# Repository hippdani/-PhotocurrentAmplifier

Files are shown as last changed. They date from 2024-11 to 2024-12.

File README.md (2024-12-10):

# Documentation of Photocurrent Sampling Amplifier
## Daniel Hipp, TU Graz 2024
This document contains a detailed description of how to build and use a transimpedance amplifier that is specifically 
tuned to the task of photocurrent sampling (PhotCurrentSampingAmplifier = PCSA). A more concise description containing the minimum information to build and 
operate the device is contained in 
[QuickGuidePCSA_EN.pdf](https://github.com/hippdani/PhotocurrentAmplifier/blob/main/QuickGuidePCSA_EN.pdf).
More information on the design process is available in the bachelor thesis ‘Photocurrent Sampling in free Air’ by 
Daniel Hipp. Files mentioned within the document are available in the repository [PhotocurrentAmplifier](https://github.com/hippdani/PhotocurrentAmplifier).

The intended use of the PCB described in here is to amplify currents produced by a strong laser field that interacts with 
some gas or material. The PCB can be operated in a fine to high vacuum to observe ions of pure gases at low pressures.
The currents are collected at the electrodes A and B and can range from pA to µA according to the amplification gain 
that is chosen. To collect 
these currents, electrodes made out of sheet metal can be soldered onto the gold plated electrodes. To prevent the electrode
elements from acting as antenna, the whole PCB should be placed inside a metal enclosure. A more detailed description of
how to ground the enclosure is contained in chapter 5 of the [documentation](https://github.com/hippdani/PhotocurrentAmplifier/blob/main/PCS_amplifier_docu_EN.pdf)

<p align="center">
  
  <br>
  Fig. 1, Inputs and Outputs on PCB
</p>

The outputs are SMA connectors with a range from +/- 2.5 V, where linearity is guaranteed up to +/- 2 V when connected 
to a load of 1k$\Ohm$ or bigger. 

The PCB displayed above can be populated in several ways to adapt its functionality:
- Electrode A will always be an input, but B can be either:
   - an input @ 0 V bias 
   - an input with a constant bias voltage
   - a bias electrode with fixed voltage 
   - a bias electrode with externally controlled bias voltage
- The transimpedance gain and bandwidth can be set for both channels individually
- A single sided or symmetrical power supply can be used
   - populate PS1 and supply +/- 2.5 V
   - populate PS2 and supply approx. 3.3 V. The negative rail will be created by a charge pump
   
The [documentation](https://github.com/hippdani/PhotocurrentAmplifier/blob/main/PCS_amplifier_docu_EN.pdf) contains detailed information 
on how to choose a configuration and calculate the component values for different gains and bandwidths.

##Low Noise Voltage Supply
To supply a potential free voltage for the PS1 configuration it is advised to either use a battery with a linear 
regulator to maintain 5 V, or a well regulated power supply with little noise. Instructions to build a low noise regulator
suited for both batteries and switch mode power supplies is contained in the folder [LowNoisePSU](https://github.com/hippdani/PhotocurrentAmplifier/tree/main/LowNoisePSU)

##Lock In Amplifier
When used to detect photocurrents generated by a pulsed laser, the signal-to-noise ratio can be vastly improved by 
using a lock in amplifier. This lock in amplifier can be set to the reference frequency of the laser pulses and will
 then reject the noise, that is not pulsed with the reference frequency. Alternatively a Boxcar averager does a similar thing.
If no commercial lock in amplifier or boxcar avergaer is at hand, consider the on described in my other [project](https://github.com/hippdani/lockInAmplifier)
(work in progress)

##Photodiode Amplifier Modification
#TODO
- upload picture / files / BOM
- describe use
- describe the photodiodes

The circuit of the PCSA is also suited to convert the photocurrent of a photodiode with little modifications. 
The modifications are necessary to accomodate the reverse bias voltage that is needed for fast operation of a photodiode.
The high pass filter that blocks out the DC from the bias forms a band pass filter together with the intrinsic low pass 
filter of the transimpedance amplifier.

The high capacity of large are (XUV-) photodiodes limits the achievable bandwidth because stability can not be achieved 
at high frequencies and high gains (Max. gain XX Ohm for Model XY photodiode to achieve 1 MHz -3dB Bandwidth).
Additionally, the large are can act as antenna for stray signals and induce oscillations on its own.
Therefore, proper shielding is required around the photodiode.

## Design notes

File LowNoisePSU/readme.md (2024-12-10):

This folder contains all relevant information to build a small linear regulated and low pass filtered voltage source 
for the photocurrent sampling amplifier. The .zip folder contains everything needed to order the PCB at a manufacturer 
(like JLC PCB, which were successfully used in the past for this design). 

It is intended to connect to a cheap switch 
mode power supply using a barrel jack connector. Such power supplies are readily available but present a lot of 
switching noise on their output. This ciruit is very effective at attenuating the differential mode noise, 
however common mode noise is not addressed.

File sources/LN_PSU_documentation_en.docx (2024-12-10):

# Low Noise Power Supply Documentation

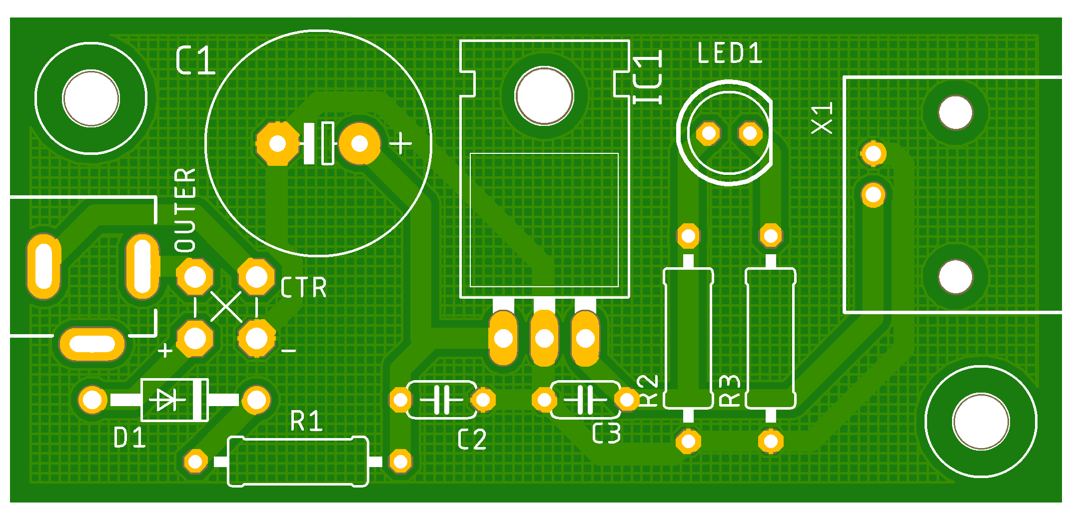
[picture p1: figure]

This PCB contains an RC lowpass filter followed by a linear regulator IC. Its purpose is to generate a stable 5 V from the noisy switch mode power supply input. It is suited to supply 5 V to the photocurrent sampling PCB (Version Jan. 2023 & Dec. 2023) and the XUV photodiode amplifier PCB Version Sep. 2023.

The maximum current that can be supplied by the LM7805 linear regulator is 500 mA. The RC lowpass filter has to be adapted to the actual current consumption of the attached device.

Calculation of R and C depending on the minimal input Voltage U_(in) and the maximum output current I_(out) :

R≤(U_(in) -5.7 V)/(I_(out) ⋅2)

C≥(0.01 s)/R

Recommendation: R=10 Ω, C=1000µF, for U_(in) > 9 V and I_(out) < 100 mA

The circuit is protected against revers polarity by a 1N4007 diode (D1). To match the polarity of the switch mode power supply and the barrel jack input, bridges can be inserted between OUTER and +,- as well as CTR and +,-. The naming OUTER and CTR is not well suited, because not all barrel jacks use the same pinout. It is advised to measure actual the connections.

# Bill of Materials

Part | Name on PCB | Availability at IEP TU Graz
BNC-Jack | X1 | Elektroniker – Lager /
LM7805 | IC1 | Elektroniker – Lager /
Electrolytic Cap. e.g. 1000 µF 25 V | C1 | Elektroniker - Lager /
Ceramic Cap. 100 nF, 50 V | C2, C3
Resistor R1, e.g. 10Ω ¼ W | R1 | Elektroniker - Lager /
Resistor approx. 500Ω ¼ W | R2 | Elektroniker - Lager /
Resistor 1kΩ ¼ W (optional) | R3 | Elektroniker - Lager /
LED 5mm (optional) | LED1 | Elektroniker - Lager /
Diode 1N4004 or 1N4007 | D1 | Elektroniker - Lager /
Barrel Jack | None (Leftmost part) | Bei Platinen / Neuhold
Screw M3x5 up to M3x9 | None | Werkstatt
Screws (2x) M3x15 or M3x20 | None | Werkstatt
3D printed housing | None

# Manufacturing

PCBs can be ordered at JLC PCB for less than 1€ per piece if 10 or more are ordered. (08.2023)
The necessary Eagle / Gerber files are supplied along with this document on Github (https://github.com/hippdani/PhotocurrentAmplifier/LowNoisePSU/LowNoisePSU_2023-09-27.zip)

Add the parts according to the BOM. LED1 and R3 are optional and only necessary if you want a power on indicator.

If less than 100 mA are supplied, bend the legs of IC1 and screw it down when assembling the PCB in the housing. If more than 100 mA are supplied, add heat conducting paste and / or a heatsink.

For mechanical robustness it is advised to glue BNC Jack X1 to the PCB (with CA glue for example). Solder in two bridges according to the polarity of the switch mode power supply used and the specific pinout of the barrel jack. Positive voltage should arrive at the hole marked + and negative at - . Configuration A and B in the following image illustrate the options.

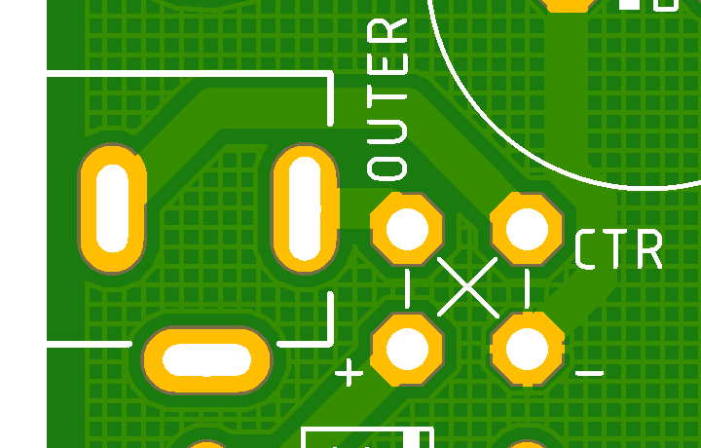
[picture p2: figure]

Print the housing according to the .3mf files (https://github.com/hippdani/PhotocurrentAmplifier/LowNoisePSU/3DPrints)supplied with this document. For better visibility of the power on indicator LED, leave the leads long above the PCB and put a diffuse transparent material onto the hole (e.g. hot glue).

Screw for fastening the PCB and IC1 to the housing: M3x5 up to M3x9

Screws for clamping the two housing halves 2 pcs..: M3x15 or M3x20

It is helpful to mark the finished Device with input voltage and polarity as well as output voltage, current and polarity.

# Electrical Characteristics

- Output voltage: 5 V ±1%, Noise < 600 µVrms typ. If attached to a switch mode PSU, < 300 µVrms typ. If attached to a Battery.
- Minimum input voltage: min. 8 V but more depending on the RC lowpass. Min 9 V if R=10 Ω, C=1000µF, I_(out) < 100 mA
- Maximum input voltage: Max. rating of capacitors or 25 V, whichever is lower.
- Maximum output current: Dictated by lowpass or max. 500 mA dictated by LM7805

# Circuit Diagram

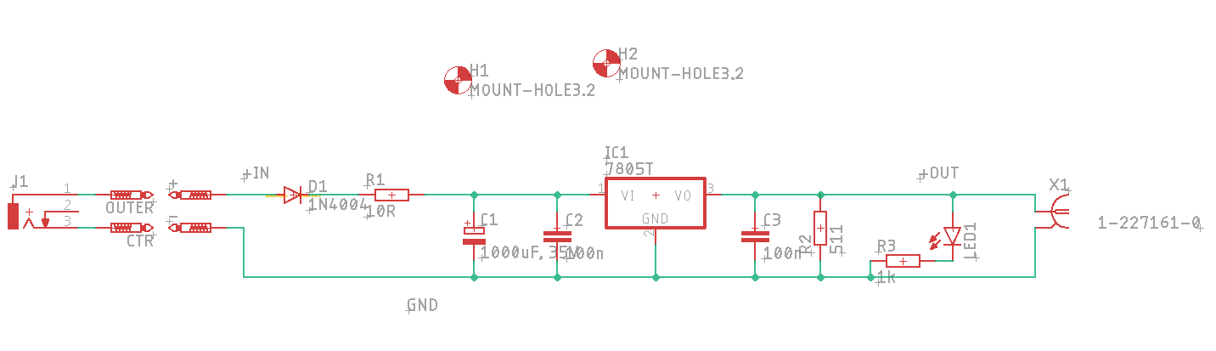
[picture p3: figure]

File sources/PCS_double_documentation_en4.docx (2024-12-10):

# Documentation of Photocurrent Sampling Amplifier

Daniel Hipp, TU Graz 2024

This document contains a detailed description of how to build and use a transimpedance amplifier that is specifically tuned to the task of photocurrent sampling. A more concise description containing the minimum information to build and operate the device is contained in ‘Quick Guide PCS PCB_en.pdf’.
More information on the design process is available in the bachelor thesis ‘Photocurrent Sampling in free Air’. Files mentioned within the document are available in this repository (https://github.com/hippdani/PhotocurrentAmplifier/).

# PCB Layout

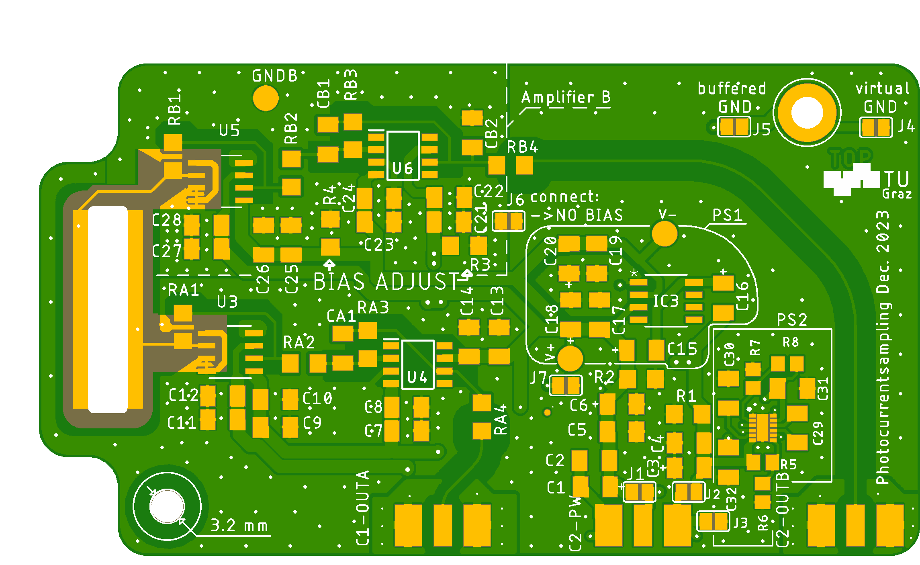
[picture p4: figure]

Electrode A

Electrode B

Output Amplifier A Power Connection Output B or Bias Voltage

The layout and circuit diagram are available as Autodesk Eagle files (PCSoposeLM.brd, PCSoposeLM.sch). In addition, Gerber files are also available in the repository.

# Intended use

The PCB and circuit can be used to amplify currents produced by a strong laser field that interacts with some gas or material (Photo Current Sampling / PCS). The PCB can be operated in a fine to high vacuum to observe ions of pure gases at low pressures.

The currents are collected at the electrodes A and B and can range from pA to µA according to the amplification gain that is chosen. To collect these currents, electrodes made out of sheet metal can be soldered onto the gold-plated electrodes. To prevent the electrode elements from acting as antenna, the whole PCB should be placed inside a metal enclosure.

The outputs are voltages with a range from +/- 2.5 V, provided on the SMA connector that corresponds to the respective amplifier / electrode (A / B). The output voltage is proportional to the input current times the gain that is set by the components. Linearity is guaranteed up to +/- 2 V when connected to a load of 1k$\Ohm$ or bigger.

# Gain Settings

Electrode A and electrode B are each connected to an independent amplification circuit. For both A and B, the same rules apply, therefore the following description uses only the component designations corresponding to A.

The overall gain is the product of the transimpedance of the first stage and the gain of the second stage.

## First Stage

The first stage or input stage consist of a LTC6268-10 in a transimpedance amplifier configuration. The value of the feedback resistor RA1 sets the TIA gain. Bigger RA1 values increase the DC-transimpedance linear, however noise is only increased proportional to √(R_(A1)) . Therefore, SNR (Signal to Noise Ratio) of DC (and slow) signals is improved with increasing RA1. The bandwidth decreases when increasing RA1, however the datasheet of LTC6268-10 is ambiguous about the proportionality:

Equation 1: f_(-3dB) ≈1/(2*π*C_(par) *R_(A1)) (Results some percent better than experiment)

Equation 2: f_(-3dB) ≈√((GBW)/(2*π*C_(par) *R_(A1))) (Results are orders of magnitude away from experiment)

Experiment data is best matched by Equation 1, which is also used for prediction of values. However, the circuit has only been tested up to 10 MHz and effects of GBW are expected to play a significant role at higher frequencies, closer to the GBW.

C_(par) ≈40-60 fF

GBW≈4 GHz (laut LTC6268-10 Datasheet)

SNR of short pulses has to be treated differently than for DC. In photocurrent sampling, packets of charge arrive at the electrodes. This event is typically shorter than what can be resolved by this amplifier and thus produces a smeared-out peak. The integral over one peak created by such an event is proportional to the amount of charge that arrived at the electrode. The signal is therefore typically recorded with a lock-in amplifier or boxcar amplifier. The amplitude of these short pulses is not only governed by the transimpedance, but also depends on the bandwidth of the amplifier, as does the noise. Higher bandwidth leads to shorter and taller peaks and in turn improves SNR.

This effect of increased bandwidth and sharper peaks (according to eq. 1) does almost cancel out the loss of DC gain when reducing RA1. This results in the value of RA1 having little influence on the amplitude of the signal pulses created by short charge packets, as long as the current to the input has a duration << 1/ f_(-3dB) . Smaller values of RA1 still affect DC transimpedance and decrease the visibility of DC input currents as well as increasing the bandwidth.

## Second Stage

Operational amplifier OPA380 in inverting configuration.

The purpose of the second stage is to decouple the sensitive output of the LTC6268-10 from capacitive or ohmic loads presented by the oscilloscope or other instruments attached to the output. At the same time, additional gain and a lowpass filter can be incorporated into the second stage.

Second stage gain: -(R_(A3))/(R_(A2))

Lowpass: f_(-3dB) ≈1/(2*π*R_(A3) *C_(A1))

A sensible approach is to set the corner frequency f_(-3dB) of the lowpass the same as the corner frequency of the first stage. This cuts away only the high frequency noise that does not contain signal. In order to achieve minimal noise while only barely compromising bandwidth, the lowpass corner frequency can be set a little bit below that of the first stage. On the other hand, a reasonable flat transfer curve and low distortion while maintaining good noise figures can be obtained when the lowpass corner frequency is set to about three times that of the first stage. The transfer function can be simulated and optimized using the LT-Spice file ‘2ndStageRCcalculator.asc’.

The values of resistor RA1 and RA2 should be at least 1 kΩ. Much bigger values will introduce additional Johnson-Nyquist noise. CA1 should be a ceramic capacitor with dielectric of type NP0 / C0G.

Overall transimpedance (DC):

Gain=R_(A1) *(R_(A3))/(R_(A2))

Currents flowing into the electrode lead to a positive voltage signal on the output. Note that electrons hitting the electrode cause a technical current flow out of the electrode.

In the following table, suggestions for component values are given. These values can be used as a starting point for experiments. Alternatively, values for various configurations are listed in file ‘Quick Guide PCS PCB_en.pdf’.

Table 1: Suggestions for component values. This will result in approximately 250 kHz bandwidth, DC-transimpedance of 10 MΩ

RA1 | 10MΩ
RA2 | 10kΩ
RA3 | 10kΩ
CA1 | 22pF

# Power Supply Settings

There are three possible ways to supply the circuit with power:

## PS1

PS1 needs a symmetrical voltage supply. The outer conductor of the connector C2-PW carries the negative voltage (-2.5 V) and the inner conductor carries the positive voltage (+2.5 V). A potential free 5V power supply is appropriate for this task, the GND voltage for the circuit is then generated by a TLE2426 rail splitter on the PCB. A well-suited power supply is described in the file ‘LowNoisePSU_doc_en.pdf’XX.

No charge pump (TLE2426) (PS1):

- J1: connect
- J2: connect
- J3: not connect
- J4 = connection of voltage divider GND to housing, OR J5 = buffered GND der of signal output to housing)
- J4 AND J5: connects internal (voltage divider) ground to output ground
- PS2 area (solid line with sharp corners) do not populate.
  - R5-R8 do not populate
  - C29-C32 do not populate
- Input voltage: J2-PW should be connected to 5V low noise voltage source, capable of providing at least 40 mA per populated amplifier (measured: A~33mA, A&B <80mA) The outer conductor of J2-PW (shielding) is at -2,5 V below ground potential, therefore only feedthroughs with floating shield can be used.

Suitable power supply: see LowNoisePSU-DokuXXXXXXX

## PS2

PS2 only requires a positive power supply (approx. 3.3 V) on the inner conductor, the positive and negative voltage of +/- 2.5 V is then generated by an LM27762 charge pump on the circuit board. With this variant, the outer conductor of the power supply has to be grounded.

This version has not been tested in a photo current sampling experiment. It seemingly worked fine in test runs in air with simulated signals. If problems occur, they most likely will stem from the switching frequency of the charge pump. With correct component values and current draw, the switching frequency should be around 2 MHz and should not adversely affect configurations with lower bandwidth.

Charge pump LM27762 (PS2):

- J1: NC
- J2: NC
- J3: connect
- J4: connect
- J5: connect
- J7: connect
- Cxx: Durch Kerko x.xuF ersetzen
- PS1 area (rounded solid line) do not populate
- PS2 area (solid line with sharp corners) populate
- do not populate R1 & R2
- do not populate TLE2624 (=IC3)
- do not populate C15-C20. However, no problem if already populated.
- Input voltage: J2-PW should be connected to a 3-5V voltage source that provides double the current as needed for a PS1 configuration. The outer conductor of J2-PW (shielding) is at ground potential, therefore grounded feedthroughs can be used.

# Bias Settings

No bias = 0 V between both electrodes / both TIA inputs:

In reality there may be a bias voltage corresponding to the difference of the offset voltages of the LTC6268-10. (UOffset << 10mV)

- J6: connect
- R1 & R2 populate both with 1 kΩ
- R3 & R4 (BIAS ADJUST): do not populate OR populate both with 1 kΩ

Fixed Bias:

- J6: NC
- Voltage divider B input bias: + R3—V_B—R4-
- Voltage divider A input bias: + R2—V_B—R1- (A-Bias only possible when using PS1)
- Deviations of the voltage dividers from 1:1 will be visible on the output as a DC component of the signal
- The sum of R of each voltage divider should be around 2 kΩ

U_(Bias_B) =U_(Betrieb) ⋅((R_4)/(R_3 +R_4)-0.5)

B electrode as variable bias:

- do not populate B-amplifier area (dashed line) except for:
- RB1 & RB2 & RB3: 0 Ω Resistor / solder bridge
- RB4 & CB2 form a lowpass to smooth the externally applied voltage. Populate with components of your liking (or choose CB2= 1uF MLCC 16V, RB4 = 10kΩ for a 16 Hz bandwidth)
- External bias can now be applied to J3-OUTB. The maximum voltage is defined by the voltage rating of CB2 but should never exceed 100 V due to sparking tendencies in low pressure atmospheres)

# Grounding

Grounding connection of the enclosure will be established via the gold plated screw hole .

This screw hole can be connected to different potentials via the jumpers J4 and J5.

Without this connection a metallic enclosure will not properly shield the circuit (from experience).

## Without Charge Pump (PS1):

- J4 = rauscharmes Spannungsteiler GND von A Verstärker wenn J6 offen / beiden Verstärkern wenn J6 verbunden ist
- J5 = gebuffertes Ground GND50 (TLE2426 =IC3) das auch an den Ausgängen mit den Shields verbunden ist.

Wenn die Ausgänge mit einem Oszi / Data Logger / etc. verbunden werden, dessen Shield Anschluss geerdet ist, ist das Problem der Masseschleifen zu beachten!

Wenn auch das Platinengehäuße geerdet ist liegt GND50 (Shieldanschluss der Ausgänge) automatisch auf Gehäusepotential. Die Verbindung ist allerdings sehr lang (Platine -> Koax -> Oszi -> Steckdose -> Laborerdung -> Labortisch -> schirmendes Gehäuse) und kann daher Brummen, Rauschen und Schwingen induzieren. Es wird zusätzlich eine kurze Erdungsverbindung z.B. über das Schraubloch und J4 / J5 benötigt. Welche Erdung bessere Ergebnisse erzielt ist noch nicht klar, ausprobieren! Ein Kurzschluss von GND50 und GND (Verbinden von J4 UND J5) ist kein Problem, es kann aber zu zusätzlichem Rauschen und Verzerrungen kommen. Das gilt immer sobald GND mit GND50 verbunden wird, egal ob direkt oder über das Gehäuse und eine Erdschleife die bei den Output Shields endet.

Empfehlung: Isolierte Gehäuse mit GND verbinden (J4 verbinden)

Geerdete Gehäuse mit GND50 verbinden (J5 verbinden) -> Erdschleifen kurz, mit kleiner Fläche und stromlos halten durch optimierte Erdung des Oszis.

## Mit Charge Pump:

Es existiert nur ein GND Potential, dieses kann über J4 und / oder J5 mit dem Gehäuse verbunden werden.

Empfehlung: Gehäuse mit GND50 verbinden (J4 verbinden, J5 verbinden)

Wenn das Gehäuse geerdet ist: Erdschleifen kurz, mit kleiner Fläche und stromlos halten durch optimierte Erdung des Oszis.

# Ein- und Ausgänge: Ratings

### Eingänge / Ausgänge von links nach rechts:

1. Ausgang Verstärker A, Innenleiter Signal, Außenleiter GND50 (Erdung)
2. Stromversorgung, Außenleiter standardmäßig (PS1) -2,5 V, Innenleiter +2,5V Alternativ (PS2): Außenleiter Erdung, Innenleiter 3,3 V
3. Ausgang Verstärker B (Innen / Außen wie A) oder Bias Signal: Außenleiter GND50 (Erdung), Innenleiter Biasspannung

### Ratings:

- Betriebsspannung ohne Charge Pump: min 4 V – max 5,25 V (5V recommended)
- Betriebsspannung mit Charge Pump: min – max V -> V max kann im Vakuum zu thermischer Überlast führen.
- Biasspannung Eingang: wenn anstatt von Verstärker B konfiguriert: Max Rating von CB2 oder max 100V
- Elektroden: Eingangsratings des LTC6268-10 kommen zur Anwendung:
  - „The inputs are protected by two series connected ESD protection

diodes to each power supply. The input current should be limited to less

than 1mA. The input voltage should not exceed 200mV beyond [above or below] the power supply. “

  - “To prevent breakdown of internal devices in the input stage, the two op amp inputs should NOT be separated by more than 2.0V. To help protect the input stage, internal circuitry will engage automatically if the inputs are separated by >2.0V and input currents will begin to flow. In all cases, care should be taken so that these currents remain less than 1mA. Additionally, if only one input is driven, internal circuitry will prevent any breakdown condition under transient conditions. The worst-case differential input voltage usually occurs when the +input is driven and the output is accidentally shorted to ground while in a unity gain configuration.” Die Eingänge können im Fall eines gesättigten Ausganges um mehr als 2 V separiert werden. Die Photoströme sind üblicherweise << 1mA und daher kein Problem, andere Ströme sollten aber unbedingt vermieden werden.
- Stromaufnahme:

Stromanforderungen an den Ausgängen + Ruhestrom:

  - 1 Verstärker, keine Charge Pump: (26 - 35) mA
  - 1 Verstärker, Charge Pump @ 5 V Input:
  - 1 Verstärker, Charge Pump @ 3 V Input:
  - 2 Verstärker, Charge Pump @ 5 V Input:
  - 2 Verstärker, keine Charge Pump: ~64mA ?
- Ausgangscharakteristik:
  - Max. Ausgangsspannung: ±(U_(Betrieb))/2
  - Max. Verzerrungsfreie Ausgangsspannung: ±(U_(Betrieb))/2-0.5 V
  - Max. Ausgangsstrom:
    - 10 mA (Verzerrungsfrei)
    - 50 mA (Reduzierte Verzerrungsfreie Ausgangsspannung)
    - 80 mA(Kurzschluss ohne Charge Pump – ohne Kühlung nur Kurzzeitig erlaubt)
    - 150 mA (Kurzschluss mit Charge Pump – ohne Kühlung nur Kurzzeitig erlaubt)
  - Empfohlener Abschlusswiderstand: >= 1 kΩ
  - Max Kapazität am Ausgang: ~100 pF, abhängig vom Abschlusswiderstand

# Bauteilempfehlungen

Metallfilmwiderstände haben minimales thermisches Rauschen aller erhältlicher SMD-Widerstandsarten. Weil Metallfilmwiderstände jedoch nicht in jeder Größe erhältlich sind, muss man manchmal zu Dünnfilmwiderständen greifen. Diese sind besser als Dickfilmwiderstände. Auf alle 1206 Footprints passen auch 0805 Widerstände. Eine Ausnahme bilden dabei RA1 und RB1, hier muss bei der Montage von 0805 besonders Acht gegeben werden den darunter liegenden Erdungsstreifen nicht zu kontaktieren. 0805 könnte an dieser Position zu erhöhter parasitärer Kapazität und damit kleinerer Bandbreite führen, genau Testergebnisse liegen jedoch nicht vor. Mehr dazu im LTC6268-10 Datasheet und im Demo Manual alias Guideline von LTC.

Alle Kondensatoren im Signalpfad sollten Keramikkondensatoren mit dem Dielektrikum NP0 / C0G sein und ein Spannungsrating >> 10V aufweisen. Kondensatoren auf den Supply Lines sollten möglichst niederohmig sein, dafür sind jeweils Paare aus kleinen Keramikkondensatoren (10 nF, 100 nF) und großen Tantal Elektrolyt Kondensatoren vorgesehen (1 µF, 2.2 µF, 10 µF). Hierbei können alle 2.2 µF Kondensatoren immer auch mit 10 µF bestückt werden.

Die Kondensatoren der Charge Pump (SP2) müssen eigene Kriterien erfüllen
Keramik MLCC X7R mit niedrigem ESR werden im Datenblatt des LM27762 empfohlen.

Der für PS1 benötigte Rail-Splitter IC TLE2426 hat während des Projekts den End-Of-Life Status erreicht und ist nur noch für begrenzte Zeit erhältlich. Ein Vorrat von 10 Stück (Feb. 2024) befindet sich im Büro von Daniel Hipp.

Update Dec. 2024: TLE2426 has status active on Ti product page and is still readily available.

# Jumper Netze

Netznamen: PWR+ …Innenleiter des C2-PWR Eingangs, PWR-….Außenleiter des C“-PWR Eingangs, V+…Positive Spannungsversorgung für Schaltung / ICs, V-…Negative Spannungsversorgung der Schaltung / ICs, GND 50….Außenleiter der Ausgänge(wird bei PS1 von TLE2426 erzeugt), GND Amp.A / Amp. B …. GND um den jeweiligen Verstärker, normalerweise durch Spannungsteiler erzeugt

- J1: verbindet PWR+ mit V+
- J2: verbindet PWR- und V-
- J3: verbindet PWR- und GND Amp. A
- J4: verbindet Schraubloch mit GND von Amp. A (Spannungsteiler-GND)
- J5: verbindet Schraubloch mit GND 50 (von TLE2426 wenn PS1)
- J6: verbindet GND von Amp. A mit GND von Amp. B
- J7: verbindet GND von Amp. A mit GND 50

# Cleaning

Bevor using the PCB in a vacuum environment, cleaning of the flux residues from soldering is necessary to prevent outgassing. Well suited for this task is the PCB cleaner “FLU, FLUXCLENE, FLU400DB” manufactured by Electrolube, which is a solvent spray can with an attached brush to loosen the residue. This rough cleaning should be followed by an ultrasonic cleaning bath in isopropyl alcohol, in order to clean under the chips and other components. After the bath the isopropyl alcohol should be allowed enough time to evaporate bevor putting the PCB in a vacuum. Otherwise boiling of the isopropyl alcohol that may be solved in the polymer casings could cause cracks in the components.

# Version Identification

The PCB discussed in this document is labelled „Photocurrentsampling Dec. 2023“and is displayed in the following figure:

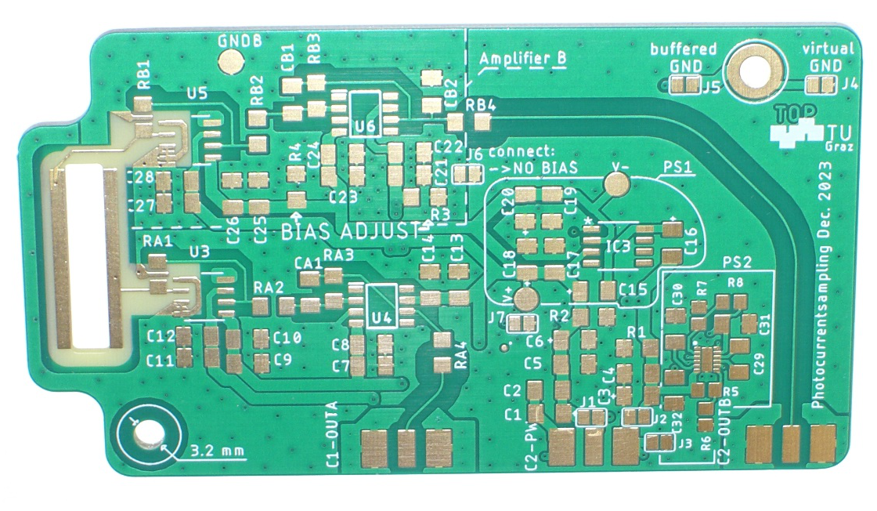
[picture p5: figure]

Die verschiedenen Bestückungsversionen lassen sich anhand der Jumper bzw. der Bestückung unterscheiden. PS1 oder PS2 ist an den entsprechend markierten Bereichen zu erkennen. Ob Amplifier B oder Bias ausgestattet ist, ist im strichlierten Bereich links oben zu erkennen. Wenn nur RB1 – RB4 und CB2 bestückt, dann ist es eine Platine mit externem Bias. Wenn dort auch ICs bestückt sind, ist ein Verstärker B verbaut.

An older version of the PCB, which is functionally identical to a configuration with PS1 and external bias voltage on electrode B is labelled: „V1, Jan. 2023 D. Hipp“. This older version is documented in the bachelor thesis XXXXXXX. The following image shows this version:

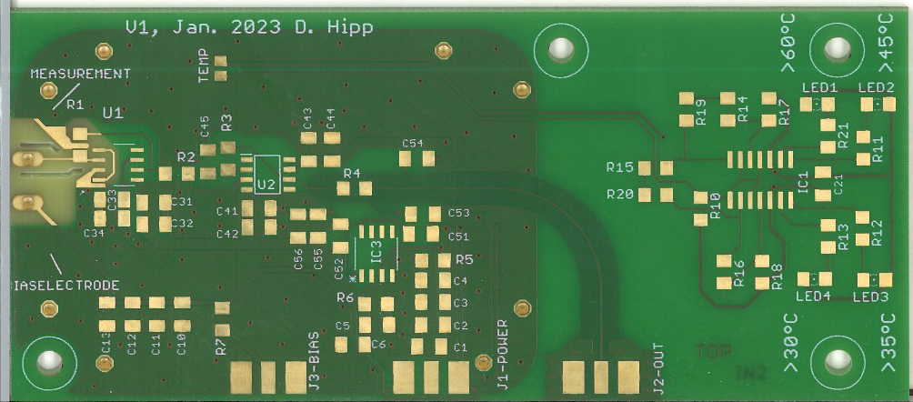
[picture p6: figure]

Both screw holes are on the same positions as in the Version Dec. 2023.

# PCB assembly

Populate the PCB according to the configuration you have chosen. The components are listed in the bill of materials: “BOM_Photocurrentsampling_Double.xlsx”

Sheet metal electrodes can be soldered to the input electrodes. Keep in mind that the material can affect the measurement with its work function and a possibly insulating oxide layer.

Some of the 10 µF capacitors are missing the polarity marking (+) on the PCB silkscreen. The polarity of those is marked in the following picture:

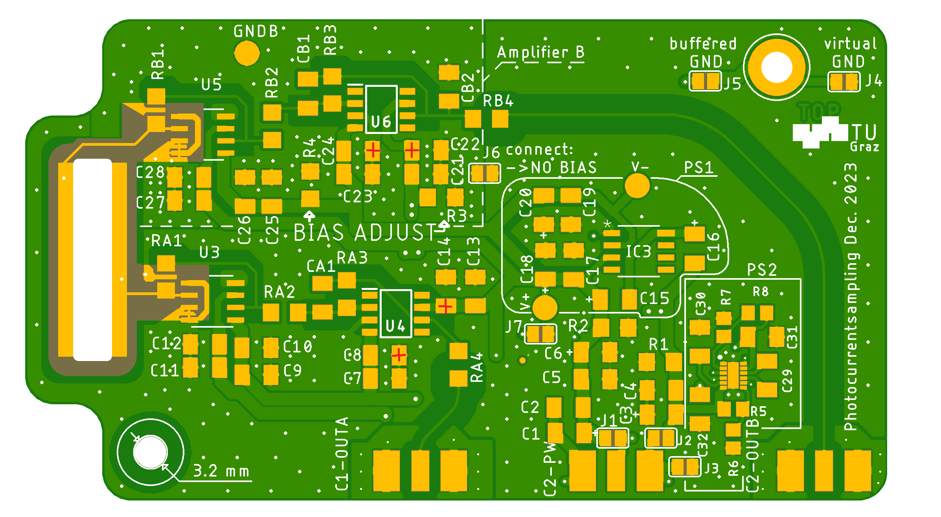
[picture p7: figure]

# ToDo:

- Bilder, bestückt,
- Schaltplan!!!

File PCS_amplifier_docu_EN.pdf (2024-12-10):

# Documentation of Photocurrent Sampling Amplifier

Daniel Hipp, TU Graz 2024

This document contains a detailed description of how to build and use a transimpedance amplifier that is specifically tuned to the task of photocurrent sampling. A more concise description containing the minimum information to build and operate the device is contained in ‘Quick Guide PCS PCB_en.pdf’. More information on the design process is available in the bachelor thesis ‘Photocurrent Sampling in free Air’. Files mentioned within the document are available in this repository. (https://github.com/hippdani/PhotocurrentAmplifier/)

## Content

Reinigung | Fehler! Textmarke nicht definiert.
Versionsidentifikation | Fehler! Textmarke nicht definiert.
Bestückung | Fehler! Textmarke nicht definiert.

## PCB Layout

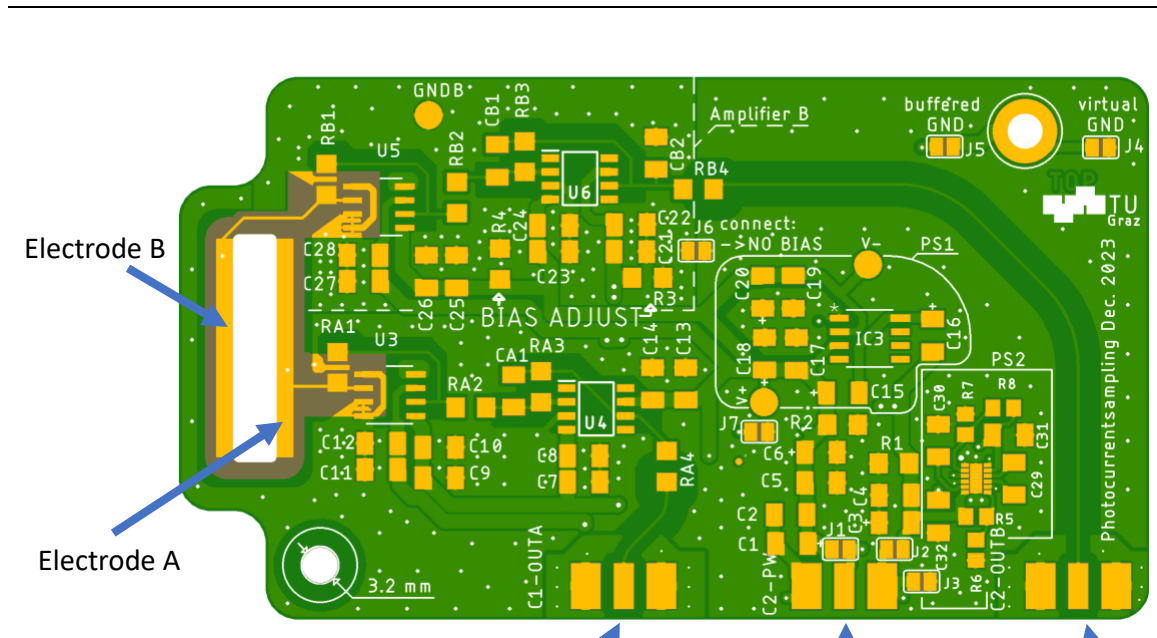
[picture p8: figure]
Electrode A; Electrode B

The layout and circuit diagram are available as Autodesk Eagle files (PCSoposeLM.brd, PCSoposeLM.sch). In addition, Gerber files are also available in the repository.

## Intended use

The PCB and circuit can be used to amplify currents produced by a strong laser field that interacts with some gas or material (Photo Current Sampling / PCS). The PCB can be operated in a fine to high vacuum to observe ions of pure gases at low pressures.

The currents are collected at the electrodes A and B and can range from pA to µA according to the amplification gain that is chosen. To collect these currents, electrodes made out of sheet metal can be soldered onto the gold-plated electrodes. To prevent the electrode elements from acting as antenna, the whole PCB should be placed inside a metal enclosure.

The outputs are voltages with a range from +/- 2.5 V, provided on the SMA connector that corresponds to the respective amplifier / electrode (A / B). The output voltage is proportional to the input current times the gain that is set by the components. Linearity is guaranteed up to +/- 2 V when connected to a load of 1k$\Ohm$ or bigger.

## Gain Settings

Electrode A and electrode B are each connected to an independent amplification circuit. For both A and B, the same rules apply, therefore the following description uses only the component designations corresponding to A.

The overall gain isthe product of the transimpedance of the first stage and the gain of the second stage.

First Stage
The first stage or input stage consist of a LTC6268-10 in a transimpedance amplifier configuration. The value of the feedback resistor RA1 sets the TIA gain. Bigger RA1 values increase the DC-transimpedance linear, however noise is only increased proportional to √RA1. Therefore, SNR (Signal to Noise Ratio) of
Output Amplifier A | Power Connection | Output B or Bias Voltage

DC (and slow) signals is improved with increasing RA1. The bandwidth decreases when increasing RA1, however the datasheet of LTC6268-10 is ambiguous about the proportionality:

Equation 1: f−3dB ≈

1
2∗π∗Cpar∗RA1

(Results some percent better than experiment)

Equation 2: f−3dB ≈ √
GBW
2∗π∗Cpar∗RA1

(Results are orders of magnitude away from experiment)

Experiment data is best matched by Equation 1, which is also used for prediction of values. However, the circuit has only been tested up to 10 MHz and effects of GBW are expected to play a significant role at higher frequencies, closer to the GBW.

Cpar ≈ 40 − 60fF

GBW ≈ 4 GHz (laut LTC6268-10 Datasheet)

SNR of short pulses has to be treated differently than for DC. In photocurrent sampling, packets of charge arrive at the electrodes. This event is typically shorter than what can be resolved by this amplifier and thus produces a smeared-out peak. The integral over one peak created by such an event is proportional to the amount of charge that arrived at the electrode. The signal is therefore typically recorded with a lock-in amplifier or boxcar amplifier. The amplitude of these short pulses is not only governed by the transimpedance, but also depends on the bandwidth of the amplifier, as does the noise. Higher bandwidth leads to shorter and taller peaks and in turn improves SNR.

This effect of increased bandwidth and sharper peaks (according to eq. 1) does almost cancel out the loss of DC gain when reducing RA1. This results in the value of RA1 having little influence on the amplitude of the signal pulses created by short charge packets, as long as the current to the input has a duration << 1/f−3dB. Smaller values of RA1 still affect DC transimpedance and decrease the visibility of DC input currents as well as increasing the bandwidth.

Second Stage
Operational amplifier OPA380 in inverting configuration.

The purpose of the second stage is to decouple the sensitive output of the LTC6268-10 from capacitive or ohmic loads presented by the oscilloscope or other instruments attached to the output. At the same time, additional gain and a lowpass filter can be incorporated into the second stage.

Second stage gain: −

RA3

RA2

Lowpass: f−3dB ≈

1
2∗π∗RA3∗CA1
A sensible approach is to set the corner frequency f−3dB of the lowpass the same as the corner frequency of the first stage. This cuts away only the high frequency noise that does not contain signal. In order to achieve minimal noise while only barely compromising bandwidth, the lowpass corner frequency can be set a little bit below that of the first stage. On the other hand, a reasonable flat transfer curve and low distortion while maintaining good noise figures can be obtained when the lowpass corner frequency is set to about three times that of the first stage. The transfer function can be simulated and optimized using the LT-Spice file ‘2ndStageRCcalculator.asc’.

The values of resistor RA1 and RA2 should be at least 1 kΩ. Much bigger values will introduce additional Johnson-Nyquist noise. CA1 should be a ceramic capacitor with dielectric of type NP0 / C0G.

Overall transimpedance (DC):

Gain = RA1 ∗

RA3

RA2

Currents flowing into the electrode lead to a positive voltage signal on the output. Note that electrons hitting the electrode cause a technical current flow out of the electrode.

In the following table, suggestions for component values are given. These values can be used as a starting point for experiments. Alternatively, values for various configurations are listed in file ‘Quick Guide PCS PCB_en.pdf’.

Table 1: Suggestions for component values. This will result in approximately 250 kHz bandwidth, DC-transimpedance of 10 MΩ

RA1 | 10MΩ
RA2 | 10kΩ
RA3 | 10kΩ
CA1 | 22pF

## Power Supply Settings

There are three possible ways to supply the circuit with power:

PS1
PS1 needs a symmetrical voltage supply. The outer conductor of the connector C2-PW carries the negative voltage (-2.5 V) and the inner conductor carries the positive voltage (+2.5 V). A potential free 5V power supply is appropriate for this task, the GND voltage for the circuit is then generated by a TLE2426 rail splitter on the PCB. A well-suited power supply is described in the file ‘LowNoisePSU_doc_en.pdf’XX.

No charge pump (TLE2426) (PS1):

- J1: connect
- J2: connect
- J3: not connect
- J4 = connection of voltage divider GND to housing, OR J5 = buffered GND der of signal output to housing)
- J4 AND J5: connects internal (voltage divider) ground to output ground
- PS2 area (solid line with sharp corners) do not populate.
- R5-R8 do not populate
- C29-C32 do not populate
- Input voltage: J2-PW should be connected to 5V low noise voltage source, capable of providing at least 40 mA per populated amplifier (measured: A~33mA, A&B <80mA) The outer conductor of J2-PW (shielding) is at -2,5 V below ground potential, therefore only feedthroughs with floating shield can be used.
Suitable power supply: see LowNoisePSU-DokuXXXXXXX

PS2
PS2 only requires a positive power supply (approx. 3.3 V) on the inner conductor, the positive and negative voltage of +/- 2.5 V is then generated by an LM27762 charge pump on the circuit board. With this variant, the outer conductor of the power supply has to be grounded.

This version has not been tested in a photo current sampling experiment. It seemingly worked fine in test runs in air with simulated signals. If problems occur, they most likely will stem from the switching frequency of the charge pump. With correct component values and current draw, the switching frequency should be around 2 MHz and should not adversely affect configurations with lower bandwidth.

Charge pump LM27762 (PS2):

- J1: NC
- J2: NC
- J3: connect
- J4: connect
- J5: connect
- J7: connect
- Cxx: Durch Kerko x.xuF ersetzen
- PS1 area (rounded solid line) do not populate
- PS2 area (solid line with sharp corners) populate
- do not populate R1 & R2
- do not populate TLE2624 (=IC3)
- do not populate C15-C20. However, no problem if already populated.
- Input voltage: J2-PW should be connected to a 3-5V voltage source that provides double the current as needed for a PS1 configuration. The outer conductor of J2-PW (shielding) is at ground potential, therefore grounded feedthroughs can be used.

## Bias Settings

No bias = 0 V between both electrodes / both TIA inputs:

In reality there may be a bias voltage corresponding to the difference of the offset voltages of the LTC6268-10. (UOffset << 10mV)

- J6: connect
- R1 & R2 populate both with 1 kΩ
- R3 & R4 (BIAS ADJUST): do not populate OR populate both with 1 kΩ

Fixed Bias:

- J6: NC
- | Voltage divider B input bias: | + R3—V_B—R4-
- | Voltage divider A input bias: | + R2—V_B—R1- (A-Bias only possible when using PS1)
- Deviations of the voltage dividers from 1:1 will be visible on the output as a DC component of
| the signal
- The sum of R of each voltage divider should be around 2 kΩ

UBiasB = UBetrieb ⋅ (

| | R4
| | R3 + R4 − 0.5)

B electrode as variable bias:

- do not populate B-amplifier area (dashed line) except for:
- RB1 & RB2 & RB3: 0 Ω Resistor / solder bridge
- RB4 & CB2 form a lowpassto smooth the externally applied voltage. Populate with components of your liking (or choose CB2= 1uF MLCC 16V, RB4 = 10kΩ for a 16 Hz bandwidth)
- External bias can now be applied to J3-OUTB. The maximum voltage is defined by the voltage rating of CB2 but should never exceed 100 V due to sparking tendencies in low pressure atmospheres)

## Grounding

Grounding connection of the enclosure will be established via the gold plated screw hole .

This screw hole can be connected to different potentials via the jumpers J4 and J5.

Without this connection a metallic enclosure will not properly shield the circuit (from experience).

Without Charge Pump (PS1):
- J4 = rauscharmes Spannungsteiler GND von A Verstärker wenn J6 offen / beiden Verstärkern wenn J6 verbunden ist
- J5 = gebuffertes Ground GND50 (TLE2426 =IC3) das auch an den Ausgängen mit den Shields verbunden ist.

Wenn die Ausgänge mit einem Oszi / Data Logger / etc. verbunden werden, dessen Shield Anschluss geerdet ist, ist das Problem der Masseschleifen zu beachten!

Wenn auch das Platinengehäuße geerdet ist liegt GND50 (Shieldanschluss der Ausgänge) automatisch auf Gehäusepotential. Die Verbindung ist allerdings sehr lang (Platine -> Koax -> Oszi -> Steckdose -> Laborerdung -> Labortisch -> schirmendes Gehäuse) und kann daher Brummen, Rauschen und Schwingen induzieren. Es wird zusätzlich eine kurze Erdungsverbindung z.B. über das Schraubloch und J4 / J5 benötigt. Welche Erdung bessere Ergebnisse erzielt ist noch nicht klar, ausprobieren! Ein Kurzschluss von GND50 und GND (Verbinden von J4 UND J5) ist kein Problem, es kann aber zu zusätzlichem Rauschen und Verzerrungen kommen. Das gilt immer sobald GND mit GND50 verbunden wird, egal ob direkt oder über das Gehäuse und eine Erdschleife die bei den Output Shields endet.

Empfehlung: Isolierte Gehäuse mit GND verbinden (J4 verbinden)

Geerdete Gehäuse mit GND50 verbinden (J5 verbinden) -> Erdschleifen kurz, mit kleiner Fläche und stromlos halten durch optimierte Erdung des Oszis.

Mit Charge Pump:
Es existiert nur ein GND Potential, dieses kann über J4 und / oder J5 mit dem Gehäuse verbunden werden.

Empfehlung: Gehäuse mit GND50 verbinden (J4 verbinden, J5 verbinden)

Wenn das Gehäuse geerdet ist: Erdschleifen kurz, mit kleiner Fläche und stromlos halten durch optimierte Erdung des Oszis.

## Ein- und Ausgänge: Ratings

Eingänge / Ausgänge von links nach rechts:
1. Ausgang Verstärker A, Innenleiter Signal, Außenleiter GND50 (Erdung)

2. Stromversorgung, | Außenleiter | standardmäßig | (PS1) | -2,5 | V, | Innenleiter | +2,5V
Alternativ (PS2): Außenleiter Erdung, Innenleiter 3,3 V
3. Ausgang Verstärker B (Innen / Außen wie A) oder Bias Signal: Außenleiter GND50 (Erdung), Innenleiter Biasspannung

Ratings:

- Betriebsspannung ohne Charge Pump: min 4 V – max 5,25 V (5V recommended)
- Betriebsspannung mit Charge Pump: min – max V -> V max kann im Vakuum zu thermischer Überlast führen.
- Biasspannung Eingang: wenn anstatt von Verstärker B konfiguriert: Max Rating von CB2 oder max 100V
- Elektroden: Eingangsratings des LTC6268-10 kommen zur Anwendung:
- „The inputs are protected by two series connected ESD protection
diodes to each power supply. The input current should be limited to less
than 1mA. The input voltage should not exceed 200mV beyond [above or below] the power supply. “
- “To prevent breakdown of internal devices in the input stage, the two op amp inputs should NOT be separated by more than 2.0V. To help protect the input stage, internal circuitry will engage automatically if the inputs are separated by >2.0V and input currents will begin to flow. In all cases, care should be taken so that these currents remain less than 1mA. Additionally, if only one input is driven, internal circuitry will prevent any breakdown condition under transient conditions. The worst-case differential input voltage usually occurs when the +input is driven and the output is accidentally shorted to ground while in a unity gain configuration.” Die Eingänge können im Fall eines gesättigten Ausganges um mehr als 2 V separiert werden. Die Photoströme sind üblicherweise << 1mA und daher kein Problem, andere Ströme sollten aber unbedingt vermieden werden.
- Stromaufnahme:
Stromanforderungen an den Ausgängen + Ruhestrom:
- 1 Verstärker, keine Charge Pump: (26 - 35) mA
- 1 Verstärker, Charge Pump @ 5 V Input:
- 1 Verstärker, Charge Pump @ 3 V Input:
- 2 Verstärker, Charge Pump @ 5 V Input:
- 2 Verstärker, keine Charge Pump: ~64mA ?
- Ausgangscharakteristik:
- Max. Ausgangsspannung: ±
| | UBetrieb
| | 2
- Max. Verzerrungsfreie Ausgangsspannung: ±
| | | UBetrieb
| | | 2 | − 0.5 V
- Max. Ausgangsstrom:
- 10 mA (Verzerrungsfrei)
- 50 mA (Reduzierte Verzerrungsfreie Ausgangsspannung)
- 80 mA(Kurzschluss ohne Charge Pump – ohne Kühlung nur Kurzzeitig erlaubt)
- 150 mA (Kurzschluss mit Charge Pump – ohne Kühlung nur Kurzzeitig erlaubt)
- Empfohlener Abschlusswiderstand: >= 1 kΩ
- Max Kapazität am Ausgang: ~100 pF, abhängig vom Abschlusswiderstand

## Bauteilempfehlungen

Metallfilmwiderstände haben minimales thermisches Rauschen aller erhältlicher SMD-Widerstandsarten. Weil Metallfilmwiderstände jedoch nicht in jeder Größe erhältlich sind, muss man manchmal zu Dünnfilmwiderständen greifen. Diese sind besser als Dickfilmwiderstände. Auf alle 1206 Footprints passen auch 0805 Widerstände. Eine Ausnahme bilden dabei RA1 und RB1, hier muss bei der Montage von 0805 besonders Acht gegeben werden den darunter liegenden Erdungsstreifen nicht zu kontaktieren. 0805 könnte an dieser Position zu erhöhter parasitärer Kapazität und damit kleinerer Bandbreite führen, genau Testergebnisse liegen jedoch nicht vor. Mehr dazu im LTC6268-10 Datasheet und im Demo Manual alias Guideline von LTC.

Alle Kondensatoren im Signalpfad sollten Keramikkondensatoren mit dem Dielektrikum NP0 / C0G sein und ein Spannungsrating >> 10V aufweisen. Kondensatoren auf den Supply Lines sollten möglichst niederohmig sein, dafür sind jeweils Paare aus kleinen Keramikkondensatoren (10 nF, 100 nF) und großen Tantal Elektrolyt Kondensatoren vorgesehen (1 µF, 2.2 µF, 10 µF). Hierbei können alle 2.2 µF Kondensatoren immer auch mit 10 µF bestückt werden.

Die | Kondensatoren | der | Charge | Pump | (SP2) | müssen | eigene | Kriterien | erfüllen
Keramik MLCC X7R mit niedrigem ESR werden im Datenblatt des LM27762 empfohlen.

Der für PS1 benötigte Rail-Splitter IC TLE2426 hat während des Projekts den End-Of-Life Status erreicht und ist nur noch für begrenzte Zeit erhältlich. Ein Vorrat von 10 Stück (Feb. 2024) befindet sich im Büro von Daniel Hipp.

Update Dec. 2024: TLE2426 has status active on Ti product page and is still readily available.

## Jumper Netze

Netznamen: PWR+ …Innenleiter des C2-PWR Eingangs, PWR-….Außenleiter des C“-PWR Eingangs, V+…Positive Spannungsversorgung für Schaltung / ICs, V-…Negative Spannungsversorgung der Schaltung / ICs, GND 50….Außenleiter der Ausgänge(wird bei PS1 von TLE2426 erzeugt), GND Amp.A / Amp. B …. GND um den jeweiligen Verstärker, normalerweise durch Spannungsteiler erzeugt

- J1: verbindet PWR+ mit V+
- J2: verbindet PWR- und V-
- J3: verbindet PWR- und GND Amp. A
- J4: verbindet Schraubloch mit GND von Amp. A (Spannungsteiler-GND)
- J5: verbindet Schraubloch mit GND 50 (von TLE2426 wenn PS1)
- J6: verbindet GND von Amp. A mit GND von Amp. B
- J7: verbindet GND von Amp. A mit GND 50

## Cleaning

Bevor using the PCB in a vacuum environment, cleaning of the flux residues from soldering is necessary to prevent outgassing. Well suited for this task is the PCB cleaner “FLU, FLUXCLENE, FLU400DB” manufactured by Electrolube, which is a solvent spray can with an attached brush to loosen the residue. This rough cleaning should be followed by an ultrasonic cleaning bath in isopropyl alcohol, in order to clean under the chips and other components. After the bath the isopropyl alcohol should be allowed enough time to evaporate bevor putting the PCB in a vacuum. Otherwise boiling of the isopropyl alcohol that may be solved in the polymer casings could cause cracks in the components.

## Version Identification

The PCB discussed in this document is labelled „Photocurrentsampling Dec. 2023“and is displayed in the following figure:

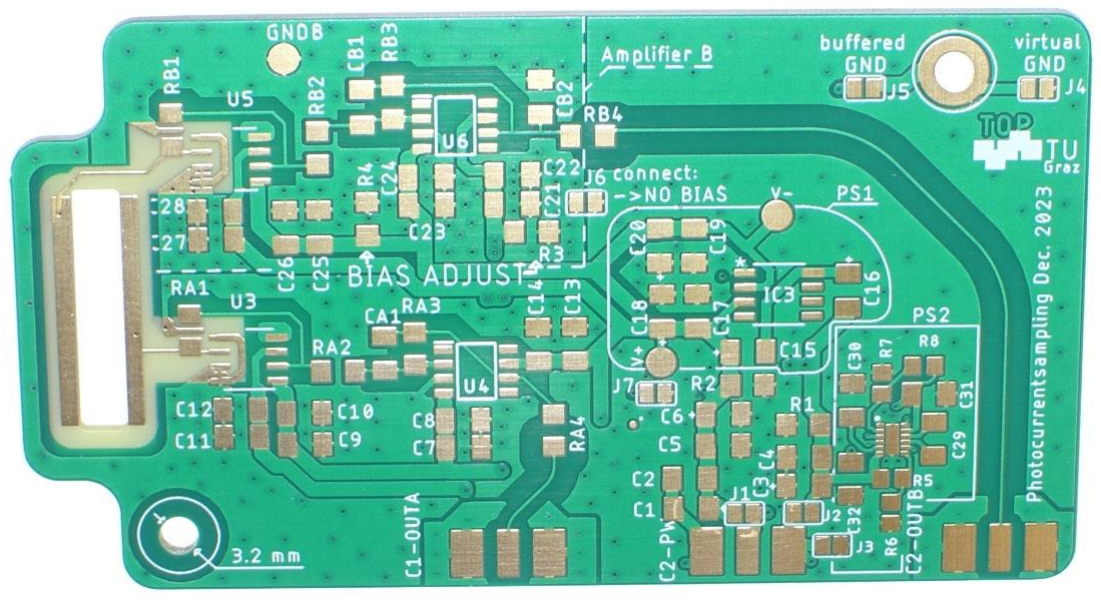
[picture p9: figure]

Die verschiedenen Bestückungsversionen lassen sich anhand der Jumper bzw. der Bestückung unterscheiden. PS1 oder PS2 ist an den entsprechend markierten Bereichen zu erkennen. Ob Amplifier B oder Bias ausgestattet ist, ist im strichlierten Bereich links oben zu erkennen. Wenn nur RB1 – RB4 und CB2 bestückt, dann ist es eine Platine mit externem Bias. Wenn dort auch ICs bestückt sind, ist ein Verstärker B verbaut.

An older version of the PCB, which is functionally identical to a configuration with PS1 and external bias voltage on electrode B is labelled: „V1, Jan. 2023 D. Hipp“. This older version is documented in the bachelor thesis XXXXXXX. The following image shows this version:

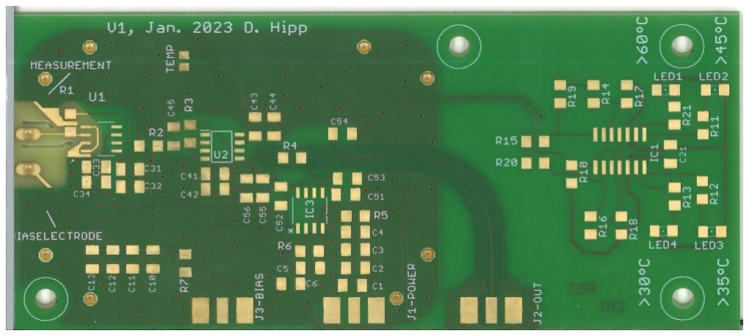
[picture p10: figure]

Both screw holes are on the same positions as in the Version Dec. 2023.

## PCB assembly

Populate the PCB according to the configuration you have chosen. The components are listed in the bill of materials: “BOM_Photocurrentsampling_Double.xlsx”

Sheet metal electrodes can be soldered to the input electrodes. Keep in mind that the material can affect the measurement with its work function and a possibly insulating oxide layer.

Some of the 10 µF capacitors are missing the polarity marking (+) on the PCB silkscreen. The polarity of those is marked in the following picture:

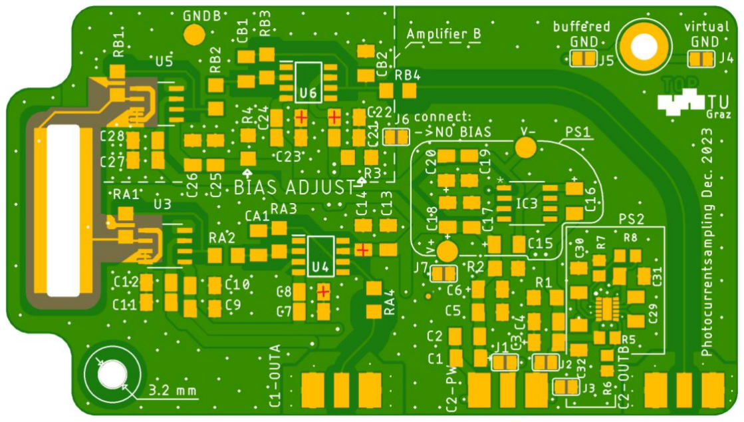
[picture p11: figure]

## ToDo:

- Bilder, bestückt,
- Schaltplan!!!

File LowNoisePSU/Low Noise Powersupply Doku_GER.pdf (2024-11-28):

# Low Noise Power Supply Doku

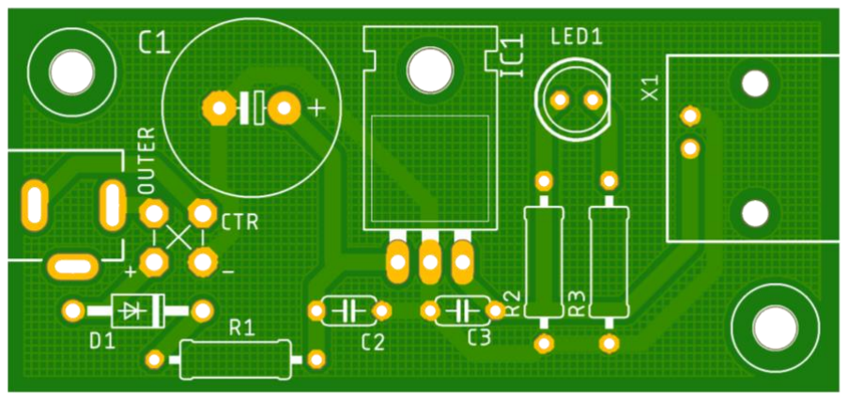
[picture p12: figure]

Es handelt sich hierbei um einen RC-Lowpassfilter mit nachfolgendem Linearregler, um aus der verrauschten Spannung eines Schaltnetzteils glatte 5 V für die Photocurrentsampling Platine oder den XUV Photodioden Verstärker zu erzeugen.

Der RC-Lowpassfilter muss auf den maximal aufkommenden Strom angepasst werden. Der LM7805 Linearregler kann ~500 mA max. liefern.

Berechnung RC in Abhängigkeit von der minimalen Eingangsspannung Uin und des maximalen Ausgangsstromes I_out :

R ≤

Uin − 5.7 V

Iout ⋅ 2

C ≥

0.01 s
R

Empfehlung: R=10 Ω, C=1000µF, für Uin > 9 V und Iout < 100 mA [?-Messung!]

Die Platine wird durch eine 1N4007 Diode vor Verpolung geschützt. Die richtige Polung des Netzteils kann durch einfügen von Brücken bestimmt werden. Dabei die verwendeten Barrel Jack Buchse auszumessen, da der Footprint nicht normiert ist. Die Platinen Beschriftung „OUTER“ und „CTR“ sind daher NICHT GÜLTIG!

## BOM

Bauteil | Bezeichnung | Quelle
BNC-Buchse | X1 | Elektroniker – Lager /
LM7805 | IC1 | Elektroniker – Lager /
Elko 1000 µF XX V | C1 | Elektronik - Lager /
Kerko 100 nF, 50 V | C2, C3
Widerstand R1, z.B. 10Ω ¼ W | R1
Widerstand ca. 500Ω ¼ W | R2
Widerstand 1kΩ ¼ W (optional) | R3
LED 5mm (optional) | LED1
Diode 1N4004 oder 1N4007 | D1
Barrel Jack | Keine | Bei Platinen / Neuhold

## Fertigung

Platinen können bei JLC PCB um <1€ pro Platine bestellt werden, bei Mengen ab ca. 10 Stück. Die nötigen Eagle / Gerber Dateien finden sich im Doku Ordner PCB.

Bestückung laut BOM, LED1 und Vorwiderstand R3 optional. IC1 Pins mit Zange Abwinkeln und bei Montage niederschrauben. Wärmeleitpaste bei I_out > 100 mA empfohlen. BNC-Buchse X1 in Montagelöcher einkleben (z.B. Sekundenkleber, CA). Brücken entsprechend dem verwendeten Netzteil und dem zugehörigen Barrel-Jack so setzen, dass positive Spannung an + liegt und negative am – Anschluss. Konfiguration A und B aus folgendem Bild verdeutlichen die Optionen:

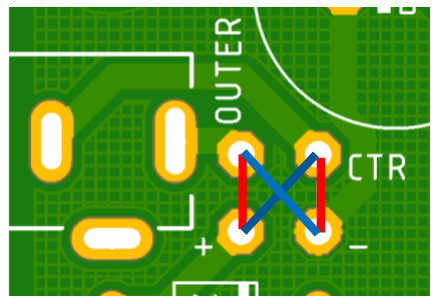
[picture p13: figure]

Gehäuse laut .3mf Files 3D Drucken. Für optimale Sichtbarkeit kann das Loch über der LED mit Heißklebe etc. gefüllt werden, um diffuse Lichtstreuung zu ermöglichen.

Schraube zur Befestigung der Platine im Gehäuse: M3x5 bis M3x9

Gehäuseschrauben 2Stk.: M3x15 oder M3x20

Pickerl mit Eingangsspannung und Ausgangsstrom sowie Steckerpolarität am Gehäuse anbringen.

## Elektrische Charakteristik

- Minimale Eingangsspannung: min. 8 V oder was durch den Lowpass und den Stromverbrauch vorgegeben wird.
- Maximale Eingangsspannung: Max Rating der Kondensatoren oder 25 V (maximum des LM7805)
- Ausgangsspannung: 5 V ± XX%, Rauschen < 600 µVrms typ. (Eine geregelte Batteriespannung hat nocheinmal ca. 50% weniger Rauschen!)
- Maximaler Ausgangsstrom: Durch Lowpass vorgegeben oder max. 500mA des LM7805.

## Schaltplan

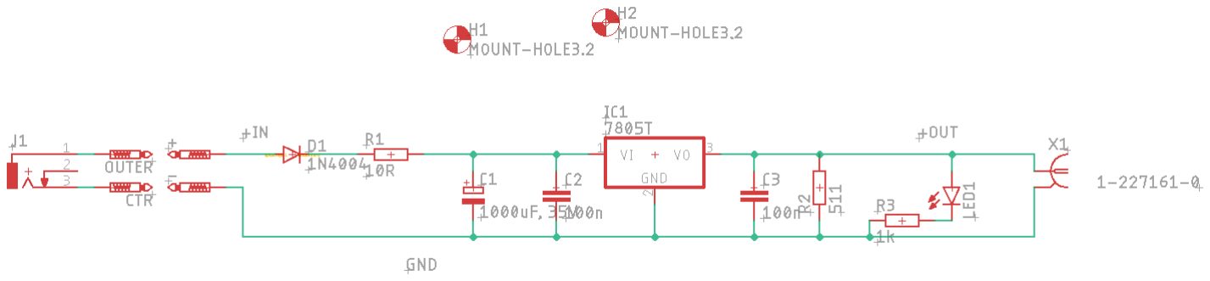
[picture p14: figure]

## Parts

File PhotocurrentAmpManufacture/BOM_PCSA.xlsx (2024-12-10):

() = variable |  | [] = optional / alternative |  | Powersupply options PS1 / PS2 | Jumper open = n, Jumper connected = y
Qty | Value | Device | Package | Parts | Description | Hersteller Nr.
2 | (10M) (100k - 100M) | R-EU_R1206 | R1206 | RA1, RB1 | Precision, thinfilm or metalfilm | ERA8AEB105V / MCA1206MD1005BP100
2 | (10k) (1k-100k) | R-EU_R1206 | R1206 | RA2, RB2 | 2nd Stage amplification feedback resistor
2 | (10k) (1k-100k) | R-EU_R1206 | R1206 | RA3, RB3 | 2nd Stage amplification feedback resistor
1 | [0-100nF] | C-EUC1206K | C1206K | CB2 | Bias Low Pass filter if no Amp2 installed
2 | (22pF) | C-EUC1206K | C1206K | CA1, CB1 | NP0 feedback kerko
2 | 50R | R-EU_R1206 | R1206 | RA4, RB4 | 47R-53R impedance matching resistor
13 | 100n | C-EUC1206K | C1206K | C2, C4, C5, C7, C9, C11, C13, C17, C19, C21, C23, C25, C27 | 10% 50V X7R | C1206C104K5RACAUTO
4 | 10n | C-EUC1206K | C1206K | C10, C12, C26, C28 | 10% 50V X7R | C1206C103K5RACTU
9 | 10uF | C-EU_POL / C-EUC1206K | C1206K | C8, C14, C22, C24, C1, C3, C6, C18, C20 | Tantal elko 1206 | TPSA106K010R0900
4 | 1k | R-EU_R1206 | R1206 | R1, R2, R3, R4 | Precision 1k 0.1% (Metalfilm, Thinfilm) | ERA8AEB102V
2 | LTC6268HS8-10PBFSO-8_S-L | LTC6268HS8-10PBFSO-8_S-L | SO-8_S-L | U3, U5
2 | OPA380AID | OPA380AID | SOIC127P600X175-8N | U4, U6 | Texas Instruments OPA380AI | OPA380AID
3 | SMA Jack | 73251-2123 | 73251-2123 | C1-OUTA, C2-OUTB, C2-PW | SMA Jack PCB Edge Mount 50 | 526-5785
4 | [100k @ PS2] | R-EU_R0805 | R0805 | R5, R6, R7, R8
3 | [1u @ PS2] | C-EUC1206K | C1206K | C29, C31, C32 | kerko switching
1 | [4.7u @ PS2] | C-EUC1206K | C1206K | C30
1 | [LM27762DSSR @ PS2] | LM27762DSSR | SON50P200X300X80-13N | PS2 | LDO Voltage Regulators and neg. switching | LM27762DSSR
2 | [1u @ PS1] | C-EU_POL | C1206K | C15, C16 | Tantal elko 1206 | TPSA105K035R3000
1 | [TLE2426 @ PS1] | TLE2426CDD8-M | D8-M | IC3
7 | () | Jumper |  | J1, J2, J3, J4, J5, J6, J7 | Select appropriate Jumpers
6 | () | Jumper PS1 |  | J1=y, J2=y, J3=n, J4 OR J5, J7=IF J4 AND J5 | Select appropriate Jumpers
6 | () | Jumper PS2 |  | J1=n, J2=n, J3=y, J4=y, J5=y, J7=y | Select appropriate Jumpers
1 | () | Jumper Amp A & B |  | J6=y | Select appropriate Jumpers
1 | () | Jumper Amp A & ext. Bias |  | J6=y | Select appropriate Jumpers
1 | () | Jumper Amp A & int. Bias |  | J6=n | Select appropriate Jumpers

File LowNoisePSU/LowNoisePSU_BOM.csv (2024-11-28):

Part | Value | Device | Package | Description
+ | PTR1PAD1-13 | PTR1PAD1-13 | P1-13 | TEST PIN
- | PTR1PAD1-13 | PTR1PAD1-13 | P1-13 | TEST PIN
C1 | 1000uF, 35V | CPOL-EUE5-13 | E5-13 | POLARIZED CAPACITOR, European symbol
C2 | 100n | C-EU050-024X044 | C050-024X044 | CAPACITOR, European symbol
C3 | 100n | C-EU050-024X044 | C050-024X044 | CAPACITOR, European symbol
CTR | PTR1PAD1-13 | PTR1PAD1-13 | P1-13 | TEST PIN
D1 | 1N4004 | 1N4004 | DO41-10 | DIODE
H1 | MOUNT-HOLE3.2 | MOUNT-HOLE3.2 | 3,2 | MOUNTING HOLE with drill center marker
H2 | MOUNT-HOLE3.2 | MOUNT-HOLE3.2 | 3,2 | MOUNTING HOLE with drill center marker
IC1 | 7805T | 7805T | TO220H | Positive VOLTAGE REGULATOR
J1 |  | DCJ0303 | DCJ0303 | DC POWER JACK
LED1 |  | LED5MM | LED5MM | LED
OUTER | PTR1PAD1-13 | PTR1PAD1-13 | P1-13 | TEST PIN
R1 | 10R | R-EU_0309/12 | 0309/12 | RESISTOR, European symbol
R2 | 511 | R-EU_0309/12 | 0309/12 | RESISTOR, European symbol
R3 | 1k | R-EU_0309/12 | 0309/12 | RESISTOR, European symbol
X1 | 1-227161-0 | 1-227161-0 | AMP_227161 | JACK, RIGHT ANGLE, 50 OHM, PCB, BNC

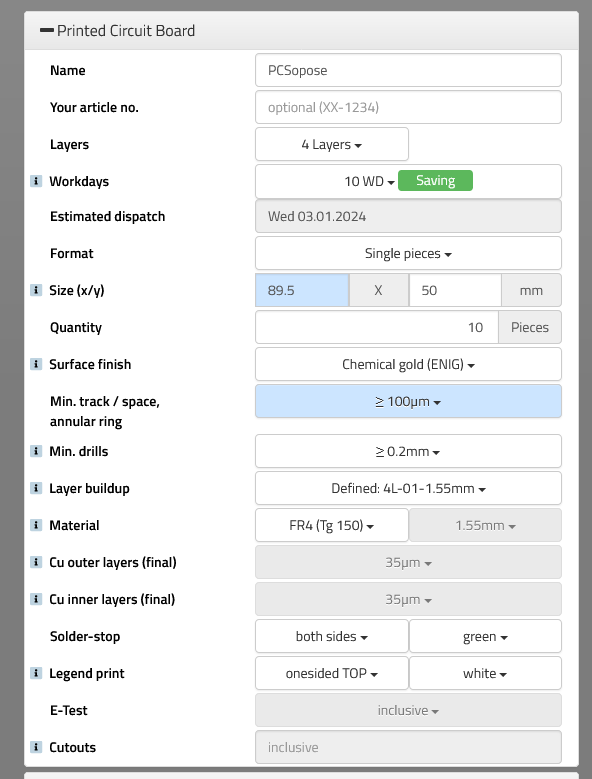
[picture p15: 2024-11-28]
PhotocurrentAmpManufacture/multicbOrderSettings.png

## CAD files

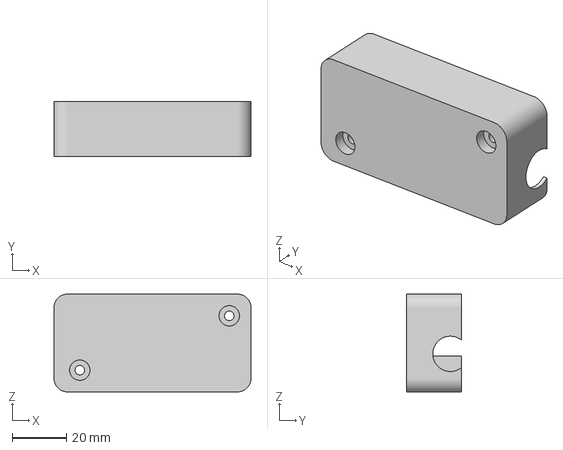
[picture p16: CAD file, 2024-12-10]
LowNoisePSU/3Dprints/BottomClampshellV2.3mf
72.5 x 20.1 x 36.0 mm

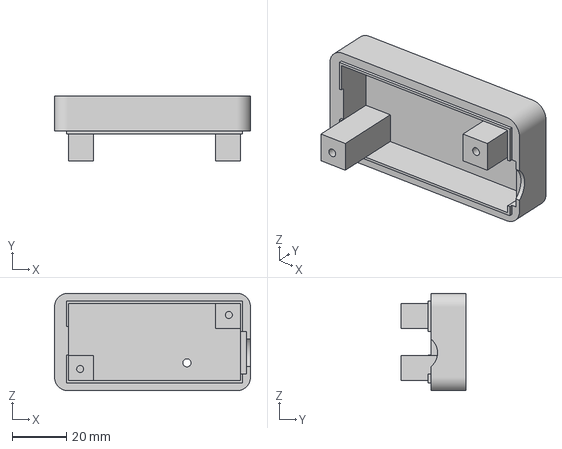
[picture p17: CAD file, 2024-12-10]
LowNoisePSU/3Dprints/TopClampshellV2.3mf
72.5 x 24.0 x 36.0 mm

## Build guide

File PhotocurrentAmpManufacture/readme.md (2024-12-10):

This folder contains all the necessary information to order the photocurrent amplifier PCB from a PCB manufacturer. 
The eagle files were used successfully to order the PCB at [multi-cb](https://www.multi-circuit-boards.eu/index.html), 
using the order details shown in this [Screenshot](https://github.com/hippdani/PhotocurrentAmplifier/multicbOrderSettings). 

The gerber files should be universally accepted by any PCB manufacturer.

The BOM contains parts for different configurations of the circuit, which ones are necessary for your build can be 
determined according to the information in [PCS_Doku](https://github.com/hippdani/PhotocurrentAmplifier/PCS_Docu.pdf). Alternatively, one of the precalculated configurations from 
the [QuickGuide](https://github.com/hippdani/PhotocurrentAmplifier/QuickGuide.pdf) can be used

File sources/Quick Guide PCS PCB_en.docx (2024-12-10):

# Quick Guide Photocurrentsampling PCB

PCB Version Dec. 2023

PCB Layout


Electrode A

Electrode B

Output Amplifier A Power Connection Output B or Bias Voltage

Each chapter of this quick guide contains all the information necessary to build and operate the circuit with the specific setting.

# Standard setting with 2 amplifiers:

~250 kHz bandwidth, DC-transimpedance of 10 MΩ, no bias between electrodes, currents of both A & B electrodes are measured.

Connect Power to the central SMA Jack. +2.5. V on the inner connector, -2.5 V on the outer side (shield). This is the same as 5V supply with positive center that is potential free, e.g. a battery or the low noise power supply described in ‘LN_PSU_documentation_en’.

The Signals are distortion free between +/- 2V but can reach up and down to the supply voltages. Terminate only with >= 1 kΩ. 1MΩ Inputs are fine without termination if the cables used are not too long.

The jumpers J4, J5 and J7 allow different grounding configurations, e.g. separating the input stage ground plane from the housing and SMA shield ground. More information on this is available in the full documentation ‘PCS_double_documentation_en’. A configuration that always works, but may be not the best solution in terms of noise is closing (connecting) jumper J4, J5 and J7.

Table 1: Bill of materials for measurement on both electrodes, ~250 kHz bandwidth, DC-transimpedance of 10 MΩ, no bias between electrodes

Qty | Value | Device | Package | Parts | Description | Hersteller Nr.
2 | 10M | R-EU_R1206 | R1206 | RA1, RB1 | Precision, thinfilm or metalfilm | ERA8AEB105V / MCA1206MD1005BP100
2 | 10k | R-EU_R1206 | R1206 | RA2, RB2 | 2nd Stage amplification feedback resistor
2 | 10k | R-EU_R1206 | R1206 | RA3, RB3 | 2nd Stage amplification feedback resistor
2 | 22pF | C-EUC1206K | C1206K | CA1, CB1 | NP0 feedback ceramic cap.
2 | 50R | R-EU_R1206 | R1206 | RA4, RB4 | 47R-53R impedance matching resistor
13 | 100n | C-EUC1206K | C1206K | C2, C4, C5, C7, C9, C11, C13, C17, C19, C21, C23, C25, C27 | 10% 50V X7R | C1206C104K5RACAUTO
4 | 10n | C-EUC1206K | C1206K | C10, C12, C26, C28 | 10% 50V X7R | C1206C103K5RACTU
9 | 10uF | C-EU_POL / C-EUC1206K | C1206K | C8, C14, C22, C24, C1, C3, C6, C18, C20 | Tantal electrolytic capacitor 1206 | TPSA106K010R0900
4 | 1k | R-EU_R1206 | R1206 | R1, R2, R3, R4 | Precision 1k 0.1% (metalfilm, thinfilm) | ERA8AEB102V
2 | LTC6268HS8-10 | LTC6268HS8-10 | SO-8_S-L | U3, U5
2 | OPA380AID | OPA380AID | SOIC | U4, U6 | Texas Instruments OPA380AI | OPA380AID
3 | SMA Jack | 73251-2123 | | C1-OUTA, C2-OUTB, C2-PW | SMA Jack PCB Edge Mount 50 | 526-5785
2 | 1u | C-EU_POL | C1206K | C15, C16 | Tantal electrolytic capacitor 1206 | TPSA105K035R3000
1 | TLE2426 | TLE2426CDD8-M | D8-M | IC3
6 | () | Jumper PS1 | | J1=y, J2=y, J3=n, J4 OR J5, J7=IF J4 AND J5 | Select appropriate Jumpers
1 | () | Jumper Amp A & B | | J6=y | Select appropriate Jumpers

# Standard setting with 1 Amplifiers + external bias:

~250 kHz bandwidth, DC-transimpedance of 10 MΩ, current of A electrode is measured, connector B is bias input.

Connect Power to the central SMA Jack. +2.5 V on the inner connector, -2.5 V on the outer side (shield). This is the same as 5V supply with positive center that is potential free, e.g. a battery or the low noise power supply described in LN_PSU_documentation_en.

The Signal is on the Left connector (A). It is distortion free between +/- 2V but can reach up and down to the supply voltages. Terminate only with >= 1 kΩ. 1MΩ Inputs are fine without termination if the cables used are not too long.

The jumpers J4, J5 and J7 allow different grounding configurations, e.g. separating the input stage ground plane from the housing and SMA shield ground. More information on this is available in the full documentation ‘PCS_double_documentation_en’. A configuration that always works, but may be not the best solution in terms of noise is closing (connecting) jumper J4, J5 and J7.

Bias can be applied to the rightmost connector (B). The shield of the connector is grounded, the inner contact carries the bias voltage. It should stay within 100V and within the voltage rating of CB2. The bias signal is lowpass-filtered by CB2 and RB4 if RB4 is not 0R.

The corner frequency of this RC lowpass is calculated by following formula:

f_(-3db) =1/(2π R_(B4) C_(B2))

The reason for the lowpass filter is to reduce high frequency noise that would create a current between the electrodes, because they form a plate capacitor. If the bias voltage will be modulated, it is important to choose a corner frequency that is much higher than the modulation frequency.

Table 2: Bill of materials for measurement on one electrode and external bias, ~250 kHz bandwidth, DC-transimpedance of 10 MΩ, bias supplied on connector B

Qty | Value | Device | Package | Parts | Description | Hersteller Nr.
2 | 10M | R-EU_R1206 | R1206 | RA1 | Precision, thinfilm or metalfilm | ERA8AEB105V / MCA1206MD1005BP100
2 | 10k | R-EU_R1206 | R1206 | RA2 | 2nd Stage amplification feedback resistor
2 | 10k | R-EU_R1206 | R1206 | RA3 | 2nd Stage amplification feedback resistor
1 | 100nF C0G | C-EUC1206K | C1206K | CB2 | Bias Low Pass filter if no Amp2 installed
2 | 22pF | C-EUC1206K | C1206K | CA1 | NP0 feedback ceramic cap.
4 | 0R | | 1206 | RB1, RB2, RB3 | 0R Jumpers or solder bridges
| 0R – 10k | | 1206 | RB4 | Bias lowpass together with CB2 or just 0R when no Lowpass is needed
2 | 50R | R-EU_R1206 | R1206 | RA4 | 47R-53R impedance matching resistor
13 | 100n | C-EUC1206K | C1206K | C2, C4, C5, C7, C9, C11, C13, C17, C19, C21, C23, C25, C27 | 10% 50V X7R | C1206C104K5RACAUTO
4 | 10n | C-EUC1206K | C1206K | C10, C12, C26, C28 | 10% 50V X7R | C1206C103K5RACTU
9 | 10uF | C-EU_POL / C-EUC1206K | C1206K | C8, C14, C22, C24, C1, C3, C6, C18, C20 | Tantal electrolytic capacitor 1206 | TPSA106K010R0900
4 | 1k | R-EU_R1206 | R1206 | R1, R2, R3, R4 | Precision 1k 0.1% (Metalfilm, Thinfilm) | ERA8AEB102V
2 | LTC6268HS8-10 | LTC6268HS8-10 | SO-8_S-L | U3, U5 | | LTC6268HS8-10
2 | OPA380AID | OPA380AID | SOIC | U4, U6 | Texas Instruments OPA380AI | OPA380AID
3 | SMA Jack | 73251-2123 | 73251-2123 | C1-OUTA, C2-OUTB, C2-PW | SMA Jack PCB Edge Mount 50 | 526-5785
2 | 1u | C-EU_POL | C1206K | C15, C16 | Tantal electrolytic capacitor 1206 | TPSA105K035R3000
1 | TLE2426 | TLE2426CDD8-M | D8-M | IC3 | | TLE2426CDD8-M
7 | () | Jumper | | J1, J2, J3, J4, J5, J6, J7 | Select appropriate Jumpers
6 | () | Jumper PS1 | | J1=y, J2=y, J3=n, J4 OR J5, J7=IF J4 AND J5 | Select appropriate Jumpers
1 | () | Jumper Amp A & ext. Bias | | J6=y | Select appropriate Jumpers

# Standard setting with 2 amplifiers and static bias

To achieve a static bias voltage between the electrodes, the input of amplifier B (LTC6268-10) is held at that bias voltage. The voltage is set by resistor R3 and R4 which form a voltage divider between +2.5V and -2.5V. The bias voltage is also added to the output signal of amplifier B, therefore reducing the available voltage swing in one direction while increasing it in the other direction.

U_(bias B) =(R_4)/(R_4 +R_3)⋅5 V-2.5 V

Scale R3 and R4 so that their parallel resistance is approximately 500 Ω.

(R_3 ⋅R_4)/(R_3 +R_4)≈500 Ω

In the same way, a static bias can be applied to the A electrode, but only if jumper J4 and J7 are open.

U_(bias A) =(R_1)/(R_1 +R_2)⋅5 V-2.5 V

Connect Power to the central SMA Jack. +2.5 V on the inner connector, -2.5 V on the outer side (shield). This is the same as 5V supply with positive center that is potential free, e.g. a battery or the low noise power supply described in ‘LN_PSU_documentation_en’.

The Signals are distortion free between +/- 2V but can reach up and down to the supply voltages. Terminate only with >= 1 kΩ. 1MΩ Inputs are fine without termination if the cables used are not too long.

The jumpers J4, J5 and J7 allow different grounding configurations, e.g. separating the input stage ground plane from the housing and SMA shield ground. More information on this is available in the full documentation ‘PCS_double_documentation_en’. A configuration that always works, but may be not the best solution in terms of noise is closing (connecting) jumper J4, J5 and J7. For static bias jumper J6 must always be open, therefore amplifier B will be surrounded by a virtual ground regardless of J4, J5 and J7.

Table 3: Bill of materials for measurement on both electrodes, ~250 kHz bandwidth, DC-transimpedance of 10 MΩ, static bias between electrodes

Qty | Value | Device | Package | Parts | Description | Hersteller Nr.
2 | 10M | R-EU_R1206 | R1206 | RA1, RB1 | Precision, thinfilm or metalfilm | ERA8AEB105V / MCA1206MD1005BP100
2 | 10k | R-EU_R1206 | R1206 | RA2, RB2 | 2nd Stage amplification feedback resistor
2 | 10k | R-EU_R1206 | R1206 | RA3, RB3 | 2nd Stage amplification feedback resistor
2 | 22pF | C-EUC1206K | C1206K | CA1, CB1 | NP0 feedback ceramic cap.
2 | 50R | R-EU_R1206 | R1206 | RA4, RB4 | 47R-53R impedance matching resistor
13 | 100n | C-EUC1206K | C1206K | C2, C4, C5, C7, C9, C11, C13, C17, C19, C21, C23, C25, C27 | 10% 50V X7R | C1206C104K5RACAUTO
4 | 10n | C-EUC1206K | C1206K | C10, C12, C26, C28 | 10% 50V X7R | C1206C103K5RACTU
9 | 10uF | C-EU_POL / C-EUC1206K | C1206K | C8, C14, C22, C24, C1, C3, C6, C18, C20 | Tantal electrolytic capacitor 1206 | TPSA106K010R0900
4 | from formula / 1k | R-EU_R1206 | R1206 | R1, R2, R3, R4 | Precision 1k 0.1% (metalfilm, thinfilm) | ERA8AEB102V
2 | LTC6268HS8-10 | LTC6268HS8-10 | SO-8_S-L | U3, U5
2 | OPA380AID | OPA380AID | SOIC | U4, U6 | Texas Instruments OPA380AI | OPA380AID
3 | SMA Jack | 73251-2123 | 73251-2123 | C1-OUTA, C2-OUTB, C2-PW | SMA Jack PCB Edge Mount 50 | 526-5785
2 | 1u | C-EU_POL | C1206K | C15, C16 | Tantal electrolytic capacitor 1206 | TPSA105K035R3000
1 | TLE2426 | TLE2426CDD8-M | D8-M | IC3
6 | () | Jumper PS1 | | J1=y, J2=y, J3=n, J4 OR J5, J7=IF J4 AND J5 | Select appropriate Jumpers
1 | () | Jumper no static bias | | J6=n | Select appropriate Jumpers

# Other options

Additional configurations are possible using the same PCB. Options include:

- other transimpedance values
- higher or lower bandwidth
- single sided power supply

a detailed description of these options and a guide how to populate the PCB if those options are chosen is available in the full documentation ‘PCS_double_documentation_en’.

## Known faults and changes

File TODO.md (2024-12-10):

- Create gerber files .zip for PCSopose and add to the Manufacture folder.

- translate last chapters of PCSA docu, fix links and recompile to pdf

- Add Old Version PCS files

- Add XUV Photodiode Amplifier docu

- Add LTspice simulation files necessary for calculations described in the PCSA docu

- add reference to bachelor thesis

- Remaster root readme.md and add links

- Do last: update links in all .docx / pdf

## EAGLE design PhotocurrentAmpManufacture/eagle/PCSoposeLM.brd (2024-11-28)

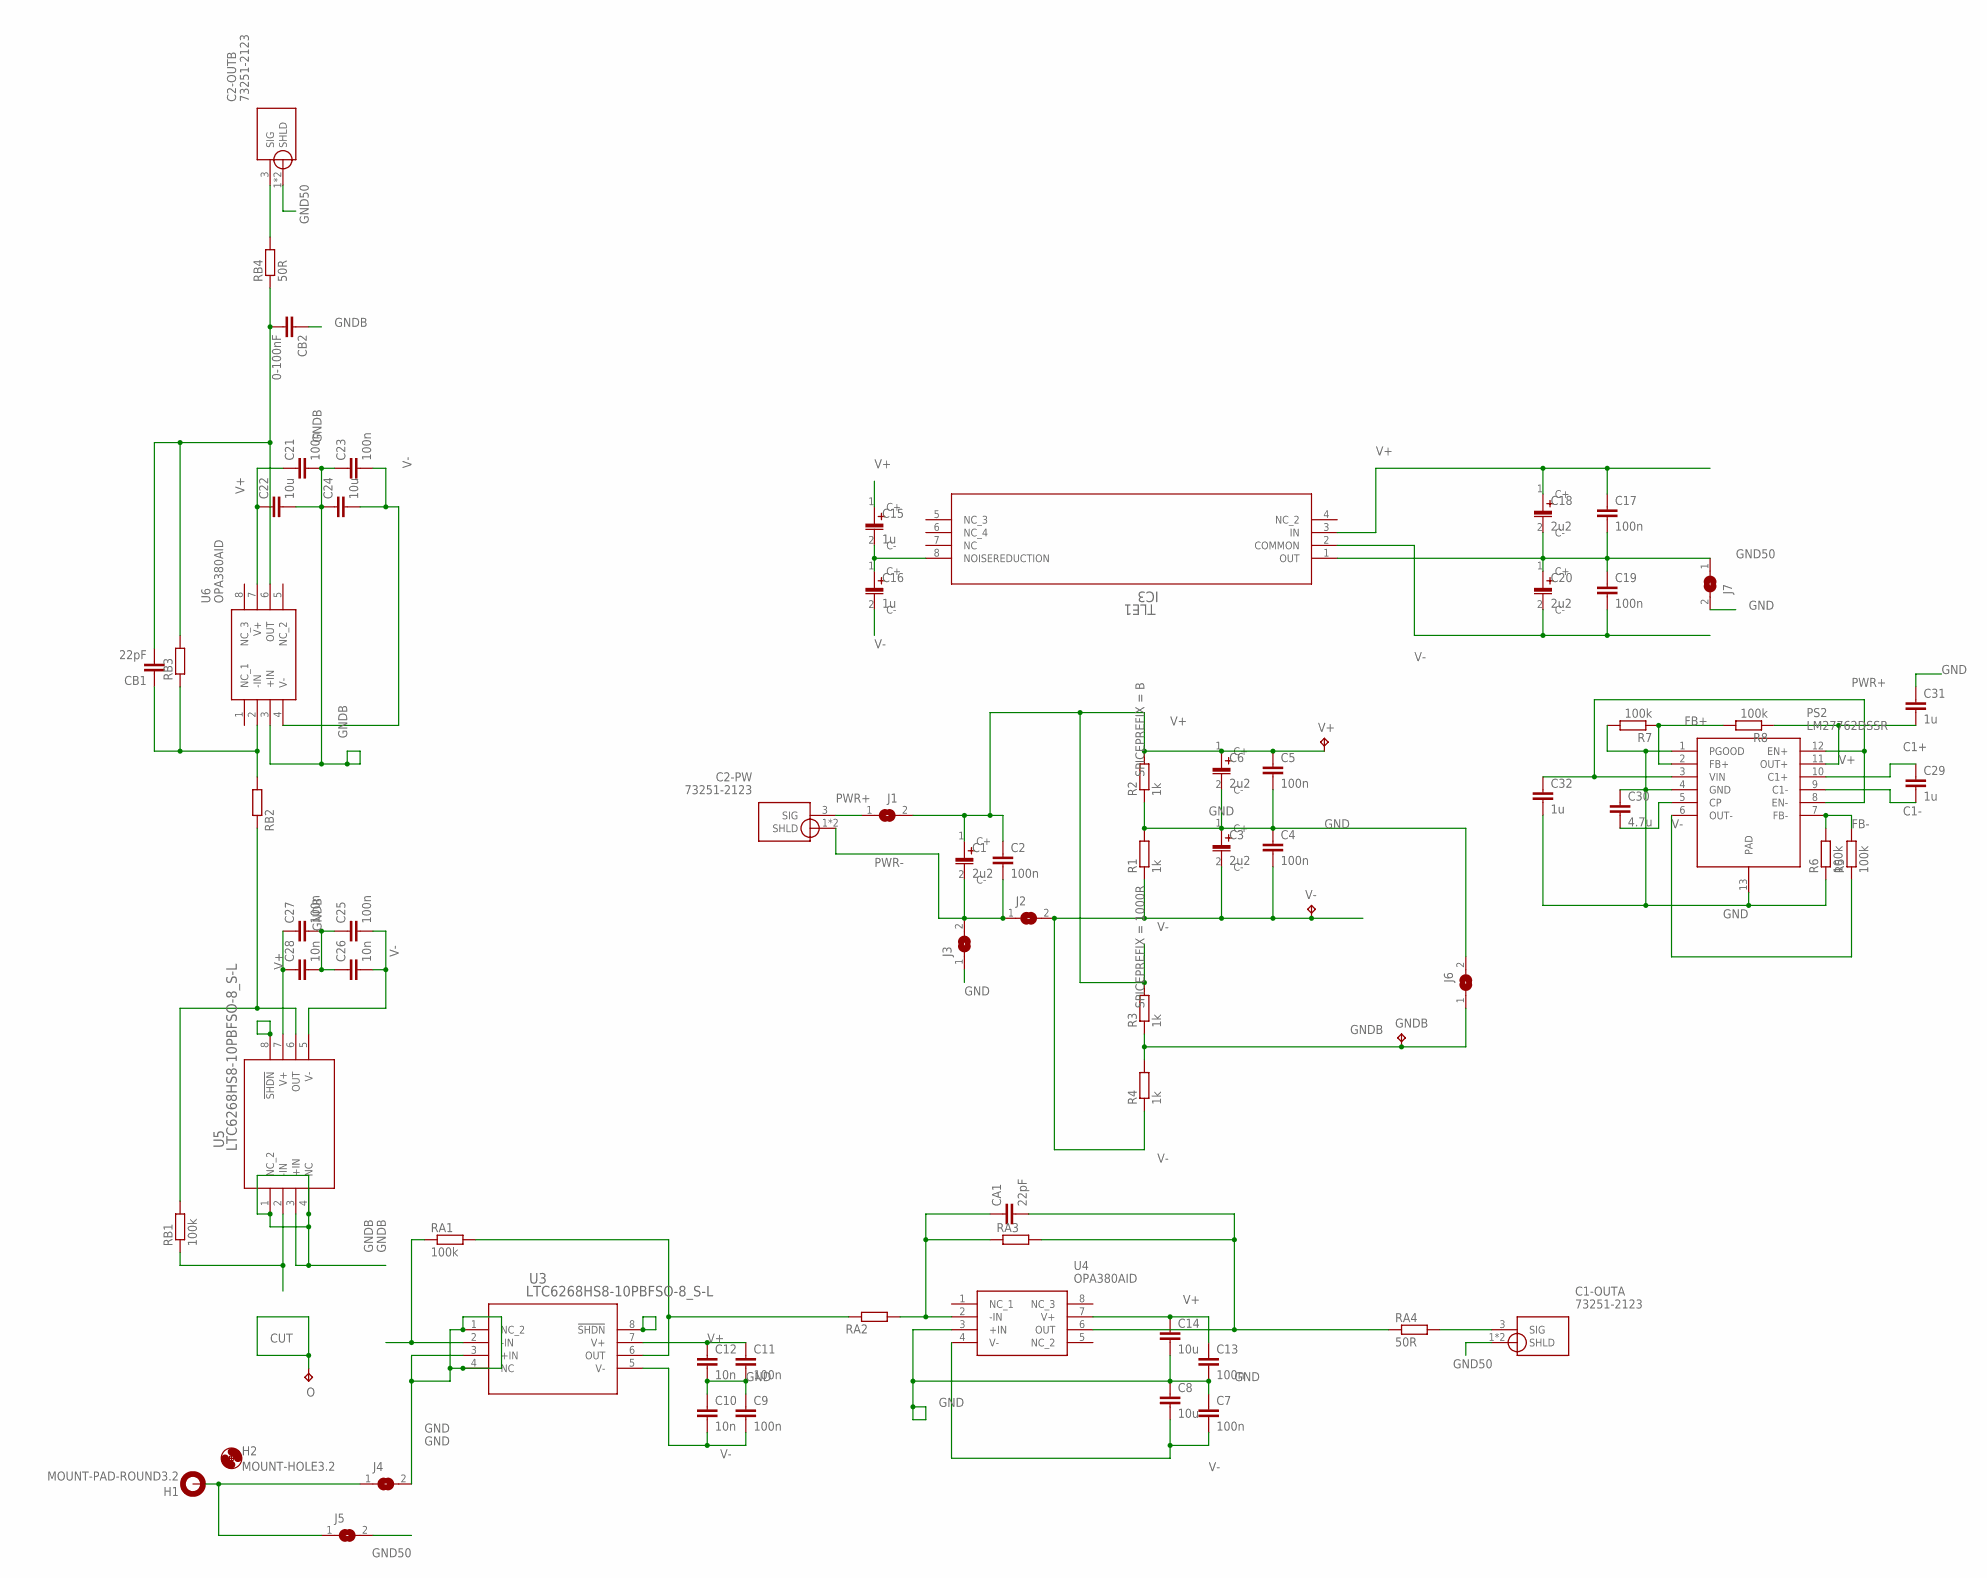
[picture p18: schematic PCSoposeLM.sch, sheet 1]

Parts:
C1, C3, C6, C18, C20: 2u2; C1206K
C1-OUTA, C2-OUTB, C2-PW: 73251-2123
C2, C4, C5, C7, C9, C11, C13, C17, C19, C21, C23, C25, C27: 100n; C1206K
C8, C14, C22, C24: 10u; C1206K
C10, C12, C26, C28: 10n; C1206K
C15, C16, C29, C31, C32: 1u; C1206K
C30: 4.7u; C1206K
CA1: 22pF; C1206K
CB1: 22pF; C1206K
CB2: 0-100nF; C1206K
GNDB: TPB2,54; B2,54
H1: MOUNT-PAD-ROUND3.2; 3,2-PAD
H2: MOUNT-HOLE3.2; 3,2
J1, J2, J3, J4, J5, J6, J7: SJ
O: TPTP06R; TP06R
PS2: LM27762DSSR; SON50P200X300X80-13N
R1, R2, R3, R4: 1k; R1206
R5, R6, R7, R8: 100k; R0805
RA1: 100k; R1206
RA2, RA3: R-EU_R1206; R1206
RA4: 50R; R1206
RB1: 100k; R1206
RB2, RB3: R-EU_R1206; R1206
RB4: 50R; R1206
TLE1: IC3; D8-M
U3, U5: LTC6268HS8-10PBFSO-8_S-L; SO-8_S-L
U4, U6: OPA380AID; SOIC127P600X175-8N
V+: TPB2,54; B2,54
V-: TPB2,54; B2,54

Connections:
C1+: C29.1, PS2.10 (C1+)
C1-: C29.2, PS2.9 (C1-)
CUT: O.TP
EXTGND: H1.B3,2, J4.1, J5.1
FB+: PS2.2 (FB+), R7.1, R8.2
FB-: PS2.7 (FB-), R5.2, R6.2
GND: C3.1 (C+), C4.1, C5.2, C6.2 (C-), C7.1, C8.1, C9.1, C10.1, C11.2, C12.2, C13.2, C14.2, C30.1, C31.1, C32.2, J3.1, J4.2, J6.2, J7.2, PS2.1 (PGOOD), PS2.4 (GND), PS2.13 (PAD), R1.2, R2.1, R6.1, R7.2, U3.1 (NC_2), U3.3 (+IN), U3.4 (NC), U4.3 (+IN)
GND50: C1-OUTA.1 (SHLD), C1-OUTA.2 (SHLD), C2-OUTB.1 (SHLD), C2-OUTB.2 (SHLD), C17.2, C18.2 (C-), C19.1, C20.1 (C+), J5.2, J7.1, TLE1.1 (OUT)
GNDB: C21.2, C22.2, C23.1, C24.1, C25.1, C26.1, C27.2, C28.2, CB2.1, GNDB.TP, J6.1, R3.1, R4.2, U5.1 (NC_2), U5.3 (+IN), U5.4 (NC), U6.3 (+IN)
INA: RA1.1, U3.2 (-IN)
INB: RB1.1, U5.2 (-IN)
unnamed: C15.2 (C-), C16.1 (C+), TLE1.8 (NOISEREDUCTION)
unnamed: RA1.2, RA2.2, U3.6 (OUT)
unnamed: C30.2, PS2.5 (CP)
unnamed: CA1.1, RA2.1, RA3.1, U4.2 (-IN)
unnamed: CA1.2, RA3.2, RA4.1, U4.6 (OUT)
unnamed: C1-OUTA.3 (SIG), RA4.2
unnamed: RB1.2, RB2.2, U5.6 (OUT)
unnamed: CB1.1, RB2.1, RB3.1, U6.2 (-IN)
unnamed: CB1.2, CB2.2, RB3.2, RB4.1, U6.6 (OUT)
unnamed: C2-OUTB.3 (SIG), RB4.2
PWR+: C2-PW.3 (SIG), C32.1, J1.1, PS2.3 (VIN), PS2.8 (EN-), PS2.12 (EN+)
PWR-: C1.2 (C-), C2.2, C2-PW.1 (SHLD), C2-PW.2 (SHLD), J2.1, J3.2
V+: C1.1 (C+), C2.1, C5.1, C6.1 (C+), C11.1, C12.1, C13.1, C14.1, C15.1 (C+), C17.1, C18.1 (C+), C21.1, C22.1, C27.1, C28.1, C31.2, J1.2, PS2.11 (OUT+), R2.2, R3.2, R8.1, TLE1.3 (IN), U3.7 (V+), U4.7 (V+), U5.7 (V+), U6.7 (V+), V+.TP
V-: C3.2 (C-), C4.2, C7.2, C8.2, C9.2, C10.2, C16.2 (C-), C19.2, C20.2 (C-), C23.2, C24.2, C25.2, C26.2, J2.2, PS2.6 (OUT-), R1.1, R4.1, R5.1, TLE1.2 (COMMON), U3.5 (V-), U4.4 (V-), U5.5 (V-), U6.4 (V-), V-.TP

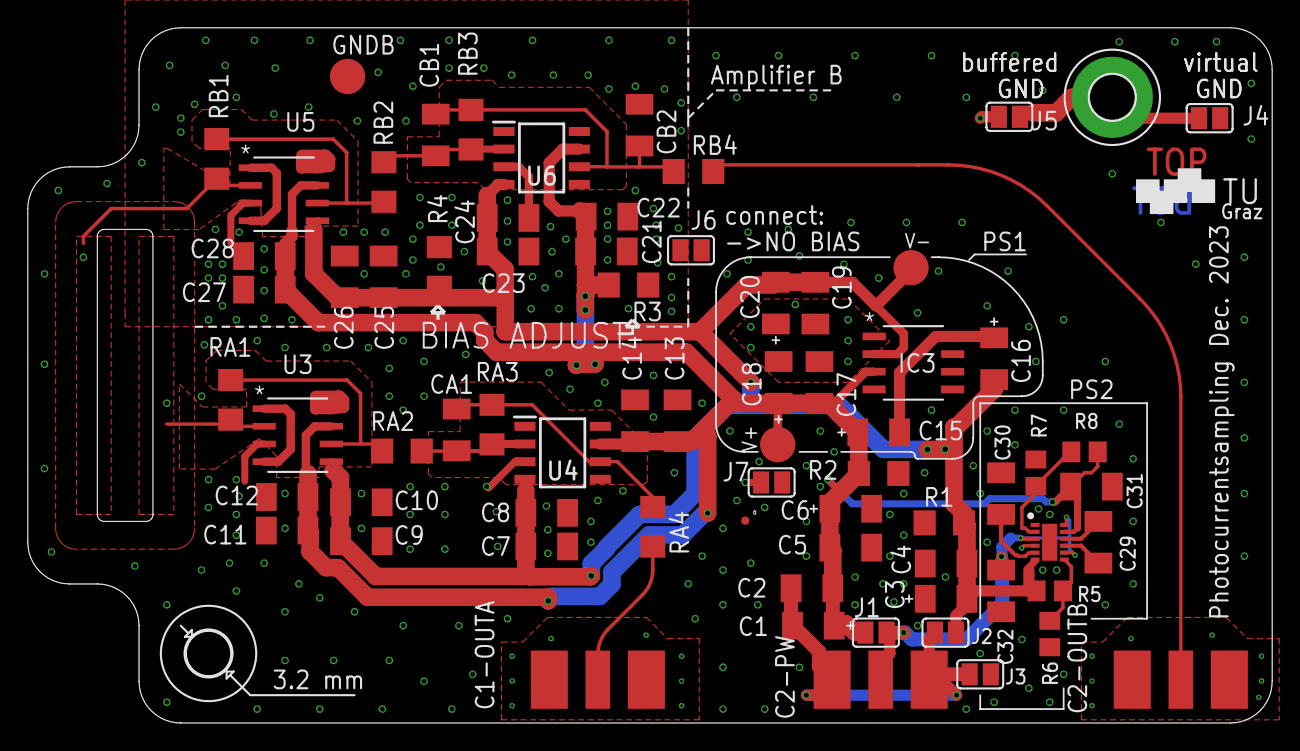
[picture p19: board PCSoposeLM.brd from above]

Board: 4 copper layers, 89.5 x 50.0 mm, 73 parts (0 on the bottom side), 24 nets.

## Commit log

2024-11-28 Add Low Noise PSU related Files via upload
    [LowNoisePSU_BOM.csv]
2024-11-28 Moved Low Noise Powersupply Doku.pdf to LowNoisePSU/Low Noise Powersupply Doku.pdf
2024-11-28 Move LowNoisePSU_BOM.csv to LowNoisePSU/LowNoisePSU_BOM.csv
    [LowNoisePSU_BOM.csv]
2024-11-28 Added PCS PCB files via upload
    [PCSoposeLM.brd, PCSoposeLM.sch]
2024-12-10 Added Quick Guide, LN:PSU_docu in english, BOM and started TODO. Added some links to the readmes
    [BOM_PCSA.xlsx]
2024-12-10 Added 3D print files
    [BottomClampshellV2.3mf, TopClampshellV2.3mf]

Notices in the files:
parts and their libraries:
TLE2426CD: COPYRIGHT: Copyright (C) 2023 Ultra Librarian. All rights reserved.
